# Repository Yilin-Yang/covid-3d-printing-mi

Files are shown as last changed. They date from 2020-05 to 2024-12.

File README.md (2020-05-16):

# COVID-19 PPE 3D Printing Resources (Michigan)

I'm using a GitHub repo as a file server/static site web host for files and
other materials useful for making or using 3D printed PPE.

If you're here to download files, then I'd recommend downloading "manually" by
clicking on the filename in the repo dashboard above, and then clicking
"Download" in the header bar (next to "History"). The files are stored with Git
LFS, so `git clone` from a terminal won't work correctly unless you have
[Git LFS](https://git-lfs.github.com/) installed.

## Where do I donate?

**I recommend donating to [Operation Face Shield](https://www.facebook.com/groups/1123320618008506/)**.
They're among the largest volunteer organizations for making and distributing 3D
printed PPE, they have several drop-off points (most in Ann Arbor, but also in
neighboring cities), and they have a far-reaching distribution network (mostly
in Michigan, but there's a pilot in the group who can make plane deliveries.
Outside of Southeast Michigan, Operation Face Shield has sent shipments to the
Upper Peninsula, Nebraska, and the Navajo Nation, among others.

**If you're 3D printing ear savers, then it would also be helpful if you
could send them to me.** I've set up an [ear saver request form](https://forms.gle/NtTunTbEoFRqz1C7A)
for individuals and small groups, but I actually blew through my entire ear
saver stockpile after the first night of the form being open.😅 Shoot me a  DM
on Facebook or an email (yiliny@umich.edu) if you'd like to donate, but need my
mailing address! **If you donate, please label your ear savers with the type of
plastic from which they were printed (PLA, PETG, ABS, etc.)!** This is normally
done by writing something like "PETG" on the plastic with a metallic Sharpie,
but you could also include a note that says "these are all PLA" or similar.

## What should I donate?

**As of the time of writing, you no longer need to 3D print faceshield
headbands.** A member of Operation Face Shield donated an injection mold for
faceshield headbands: using that mold, they can now manufacture ~1500 face
shields per day, which is orders of magnitude more than can be practically
manufactured by 3D printing. For comparison, it takes roughly 22 hours for
a single 3D printer to finish printing eight.

**Instead, I'd recommend printing "ear savers",** because that's what I
and OFS are short on right now. (UPDATED 5/15/20) Operation Face Shield
currently has a _long_ backlog of orders to fill, and would be thankful for any
help you can provide!

## Files

- [`ear_saver_thinn`](./ear_saver_thinn.stl) is the original STL provided by
  Operation Face Shield for its volunteers.
- [`ear_saver_thicc`](./ear_saver_thicc.stl) is a slightly modified version
  with a thicker band (1.5mm, rather than 1mm).

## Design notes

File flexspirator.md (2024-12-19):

# Flexspirator – Usage and Care

*Past versions of this page are visible in its [History](https://github.com/Yilin-Yang/covid-3d-printing-mi/commits/master/flexspirator.md).*



The "Flexspirator" is a Maker-made reusable respirator that _should_ provide
N100 protection, **though it has not been formally tested and certified by
NIOSH.** It passes a self-administered [OSHA 1910.134 App A "Irritant Smoke"
qualitative fit test.](https://www.osha.gov/laws-regs/regulations/standardnumber/1910/1910.134AppA)

The Flexspirator is designed to be worn daily by members of the general
population, to _protect_ themselves and others from COVID-19. It is intended to
be worn _instead_ of a regular cloth face mask or surgical mask, and should
offer strictly better protection.

## Motivation

Medical workers wear N95 respirators (or better) when treating COVID patients;
these protect them from contracting COVID-19 by inhaling coronavirus particles.
The N95 respirator filters the coronavirus particles out of the air they
inhale. If the respirator does not have an exhalation valve, then it will
_also_ filter coronavirus particles out of the air that the wearer _exhales_ as
well.

[**N95 respirators have been in shortage since the start of the pandemic.**](https://www.propublica.org/article/expired-respirators-reused-masks-nurses-in-the-nations-original-covid-19-epicenter-offer-sobering-accounts-of-what-could-come)
Standard medical practice is for medical workers to wear a disposable N95
respirator while treating a sick patient, and for them to _throw away_ that
respirator before treating another patient. Now, medical workers frequently
reuse the same "single-use" N95 respirator for days or weeks on end.

[As of October 27th,](https://www.cnbc.com/2020/10/27/3m-making-more-n95-masks-than-ever-as-covid-cases-rise.html)
current CDC guidelines ask that members of the general public do not purchase
N95 masks for their own day-to-day use, and instead wear cloth face masks
and/or surgical masks. This is to preserve the supply of disposable N95
respirators for frontline medical workers.

It is still probably unreasonable to expect the general public _not_ to seek
out respirators. As of November 13th, the American health care system is on the
verge of [nationwide collapse](https://www.theatlantic.com/health/archive/2020/11/third-surge-breaking-healthcare-workers/617091/)
due to uncontrolled COVID outbreaks across all 50 states. Members of the
general public should start wearing respirators: both to help protect
themselves from COVID-19 infection, and to reduce the resulting burden on the
nationwide health care system.

The Flexspirator is intended to help fill this gap. It has not been NIOSH
certified, and probably cannot be issued to actual healthcare workers without
violating OSHA regulations, but members of the general public can wear one
_voluntarily,_ and they should be protected from COVID-19 by doing so.

## Protection Offered

**The Flexspirator _should_ offer protection comparable to a reusable N100
respirator.**

This is better than the protection offered by an N95 respirator
and should be sufficient to protect the wearer from inhaling coronavirus
particles while properly worn.

It should also protect the wearer from inhaling any sort of fine particulates,
including smoke, sawdust, metal swarf (from grinding tools), and tear gas.

This is not the same _type_ of protection as offered by a respirator equipped
with (e.g.) P100 + activated carbon filters. Oily aerosols may destroy the
Flexspirator's HEPA filter, rendering it ineffective at filtration. The HEPA
filter will also not absorb chemical fumes, such as from spraypaint or Flex
Seal.

## Basic Construction

The Flexspirator is a slightly modified [Maker Mask Rapid](https://www.makermask.com/rapid-360.html)
printed from [clear PETG](https://www.amazon.com/OVERTURE-Filament-Transparent-Multipack-Dimensional/dp/B08344S1TT)
reinforced with a strong, flexible, rubberized coating of [Swift Response's Flex Seal
Liquid](https://www.youtube.com/watch?v=_NygbA9UYPw), the easy way to coat,
seal, and stop leaks fast. It's the super thick rubber that you can pour right
into cracks to stop COVID dead in its tracks.

Flex Seal starts out as a thick liquid and turns into a super strong flexible
rubber. Dipping 3D printed Maker Mask Rapids creates an airtight seal that
lasts for years.  This rubberized coating blocks ingress of contaminated air through
[cracks and holes in the plastic mask frame](https://www.preprints.org/manuscript/202006.0080/v1)
produced as artifacts of the [FDM printing](https://en.wikipedia.org/wiki/Fused_filament_fabrication)
process.

In extreme heat or cold, Flex Seal Liquid keeps its hold.

<details>
<summary>
⚠DO NOT EXPOSE A FLEXSPIRATOR TO PROLONGED TEMPERATURES OF GREATER THAN 65
DEGREES CELSIUS (149 DEGREES FAHRENHEIT); THIS MAY DEFORM THE PLASTIC.⚠
</summary>

A rough lower bound for the [glass transition temperature](https://en.wikipedia.org/wiki/Glass_transition)
of PETG plastic is 67 degrees Celsius, [according to Wikipedia.](https://en.wikipedia.org/wiki/Polyethylene_terephthalate)

Heating a Flexspirator past the PETG glass transition temperature will probably
cause the plastic to warp and deform.
</details>

Unlike thin paints, Flex Seal Liquid is **𝕤𝕦𝕡𝕖𝕣 𝕥𝕙𝕚𝕔𝕜** and creates a flexible
barrier that's _completely_ airtight. It's like a handyman, in a can!

Flex Seal Liquid is safe around plants and animals, so we used it to seal these
Flexspirators.

**Now with any COVID outbreak, big or small – Flex Seal shuts out aerosols!**

To show you the incredible sealing power of Flex Seal Liquid, we made an entire
respirator out of 3D printed PETG plastic, and covered it in Flex Seal Liquid.

After a day of creating irritant smoke clouds, and deliberately huffing them
while wearing a Flexspirator, Flex Seal's airtight barrier takes a beating; and
the HEPA filter, cut from an [ordinary replacement HEPA filter](https://www.amazon.com/gp/product/B00BWYNZV4/)
for a home air purfiier, stays filtrationally effective.

The inside will not be completely dry, because your breath will tend to
condense on the Flexspirator's inner surface.

<details>
<summary>
⚠LIMIT OR AVOID STRENUOUS PHYSICAL ACTIVITY WHILE WEARING A FLEXSPIRATOR
TO AVOID SOAKING THE FILTER WITH MOISTURE FROM YOUR BREATH.⚠
</summary>

Physical activity such as intense aerobic exercise requires heavy breathing.
Your breath carries moisture; too much may soak and moisten the HEPA filter
media, and cause it to clog; this will make breathing difficult or impossible,
and may or may not irreparably damage the filter.

If the activity cannot be avoided, be prepared to "hot-swap" the filter
cartridge if it clogs.
</details>

## Basic Usage

### Parts and Components

Flexspirator parts

The **Top Strap** and **Bottom Strap** secure the Flexspirator against your
face. They can be adjusted by pulling the ends of each strap through the
Slide Buckle, the Loop Buckle, or the Hook Buckle.

The **Hook Buckle** and the **Loop Buckle** on the Bottom Strap fasten
together behind your neck when you don the Flexspirator. This mimics the design
of a conventional reusable elastomeric respirator.

The **Mask Body** is the larger Flexspirator facepiece. It is comprised of
a stiff mask frame of PETG plastic coated on both its interior and exterior
with a silicone rubber coating of Flex Seal Liquid. Along with the Edge Lining,
the Mask Body makes up the **Facepiece** (not labeled).

The **Edge Lining** is the edge of the Flexspirator facepiece where it
contacts your face. It is comprised of [rubber kerf-mount weather stripping](https://www.amazon.com/gp/product/B06Y1SND8X)
coated with Flex Seal Liquid; the weather stripping is soft and can conform to
the wearer's face, while the silicone rubber Flex Seal coating improves its
seal against bare skin.

<details>
<summary>
Earlier Flexspirators used vinyl weather stripping, as specified by the Maker
Mask Rapid's original design.
</summary>

The [vinyl weather stripping](https://www.homedepot.com/p/M-D-Building-Products-1-2-in-x-17-ft-White-Vinyl-Gasket-Weatherstrip-78394/100193598)
was very stiff, making it necessary to cinch the Top Strap and Bottom Strap
uncomfortably tight in order to compress the Edge Lining against the wearer's
face firmly enough to seal.

The new rubber weather stripping is softer and more flexible, and unlike the
vinyl weather stripping, can reliably seal against a person's face even without
a silicone rubber coating of Flex Seal Liquid. Its use also makes the
Flexspirator much more comfortable to wear.
</details>

The **Filter Slot** is the hole into which the Filter Tray is placed. The space
between the Filter Tray and the Filter Slot (not labeled) is the
**Cartridge/Slot Interface**; this must be filled with a **Cartridge/Slot
Interface Sealant**, such as petroleum jelly applied to the lip of the
Filter Tray, to prevent contaminated air from flowing around and bypassing the
filter media.

The **Filter Tray** houses the **Filter Media**, which actually filters air.
The Filter Media is compressed flush against the walls of the Filter Tray by
a plastic **Retaining Ring**. Without this Retaining Ring, the Filter Media may
lift and curl away from the walls of the Filter Tray, creating air gaps, which
may allow contaminated air to bypass the Filter Media.

The **Filter Cover** is functionally a "nut" that screws onto the lip of the
Filter Tray where it protrudes beyond the front of the Flexspirator. It does
not help to filter air, but simply holds the Filter Tray snugly against the
walls of the Filter Slot. We call a Filter Cover screwed onto a Filter Tray
a **Filter Cartridge.**

The **Locking Dimple** is a small divot in the front of the Mask Body. The
Filter Cover has a corresponding **Locking Bump** that seats into the Locking
Dimple when the Filter Cover is screwed onto the Filter Tray, helping to lock
the Filter Cover into place.

### Assembly and Disassembly, Replacing Filter Cartridges

This summarizes the process of loading a new Filter Tray into the Flexspirator.
Removing an already installed Filter Tray is essentially the reverse of
this process.

**1. With the Mask Body cupped in one hand, place a Sealant-coated Filter
Tray into the Filter Slot.**



**2. Press the Filter Tray firmly into the Filter Slot.**



If you have just applied petroleum jelly Sealant to the lip of the Filter Tray,
then you should see the excess jelly squeeze out from _all_ sides of the
Cartridge/Slot Interface. If it does not, or if it squeezes out on some sides
but not on others, then remove the Filter Tray and apply more petroleum jelly
where needed.

**3. The lip of the Filter Tray should visibly protrude from the front of the
Mask Body.**



During disassembly, you can pop the Filter Tray out of the Filter Slot without
getting petroleum jelly on your hands by striking the exposed lip of the Filter
Tray with the Filter Cover.

**4. Place a Filter Cover over the lip of the Filter Tray as pictured so that
the "nubs" of the Filter Cover point toward 11 o'clock and 5 o'clock
positions.**



**5. Grip the nubs of the Filter Tray.**



**6. Twist the Filter Tray clockwise, as viewed from the front of the Mask
Body, until the Locking Bump slides into the Locking Dimple.**



You may hear or feel the Locking Bump click into place. If the Locking Bump
does not fit into the Locking Dimple because the Locking Dimple is packed with
Flex Seal, then you may scrape out the excess Flex Seal with a small pick or
knife.

**Do NOT** twist the Filter Cover so that the Locking Bump moves _past_ the
Locking Dimple. This may damage the lip of the Filter Tray.

It is possible for the Locking Bump to break off of the Filter Cover. In this
case, the Filter Cover can still be used, but may not hold the Filter Tray as
solidly. Note that Filter Covers are fully interchangeable, so a Filter Cover
from a replacement Filter Cartridge can replace a broken Filter Cover without
issue.

### Maintenance

Protect the Flexspirator from damage so that it can still maintain an
airtight seal against the wearer's face when worn.

The seal may be compromised by:

1. _Physical damage to_ OR _manufacturing defects in_ the plastic mask frame,
resulting in micro- or macro-scale cracks and holes.
2. _Peeling_ or _perforation_ of the Flex Seal coating.
3. _Pinhole leaks_ in the _filter cartridge/slot sealant_, which may allow air to
bypass the HEPA filter media by passing between the filter tray and the filter
slot.

Even the plastic mask frame should be largely airtight by
itself. This creates protective redundancy: both (1) and (2) must occur at the
same spot on the mask's surface for the walls of the mask to spring a leak.
To check for such leaks, conduct an **Integrity Test** as described below.

Of course, tears, punctures, or other forms of damage to the Filter Media can
make it ineffective at filtration. Actual holes would allow contaminants to
bypass the filter, for instance, or destroy the mesh of fine fibers in the
Filter Media that would actually trap contaminants. Take care to avoid damage
to the Filter Media when cleaning, disinfecting, or wearing the Flexspirator.

#### Avoiding Damage to the Filter Media

_When researching how to work with HEPA filter media, I used [this link](https://smartairfilters.com/en/blog/hepa-filters-make-diy-face-masks-covid-coronavirus/)
as an informational reference._

The Filter Media is cut from an ordinary replacement [HEPA
filter](https://www.amazon.com/gp/product/B00BWYNZV4/) for a household air
purifier. It consists of a stiff, "papery" structural layer of PET fibers that
supports a thin, extremely delicate "tissue" of polypropylene (PP) fibers. The PP
fibers are the "actual" filter media that would trap contaminants like
coronavirus particles. The PET backing provides some filtration, but this is
probably incidental, and for safety we should assume that the filter media is
ineffective without an intact PP "tissue".



HEPA filters intended for actual use are typically pleated, i.e. folded like an
accordion, to maximize the surface area of filter media in which contaminants
can be trapped. In filters like the [Honeywell replacement filter](https://www.amazon.com/gp/product/B00BWYNZV4/)
that I cut apart for Filter Media, each individual fold of the "accordion" is
supported by strips of thick glue from the fold underneath.

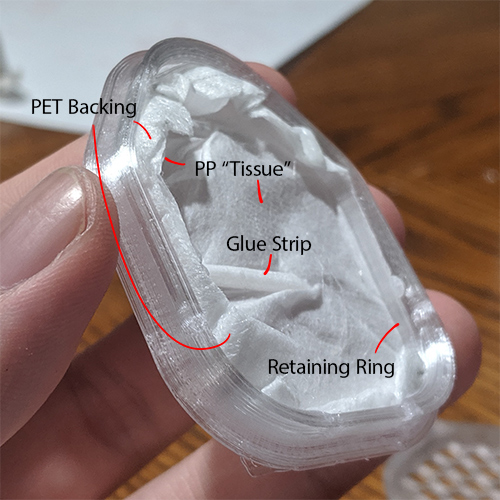
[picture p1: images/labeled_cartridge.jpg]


If you need to remove the Filter Media from a Filter Tray, then _after_
removing the Retaining Ring, you can use a thin object (like a screwdriver) to
push the Filter Media out of the tray, pressing the object's tip into a glue
strip, avoiding damage to the PP "tissue". You should also be careful to
unstick the glue strips from the inner surface of the Filter Tray "lip", if
applicable, so that the PP "tissue" does not rip as the Filter Media is removed
from the Filter Tray.

To protect the Filter Media from damage and preserve its effectiveness
at filtration:

- **Do NOT** prod or scratch at the soft, felt-like "tissue" in the Filter Tray
- **Do NOT** soak or splash the Filter Media with water or other liquids
- **Do NOT** expose the Filter Media to soaps or disinfectants
- **Do NOT** expose the Filter Media to oily, sticky, tarry, or resinous aerosols, such as
  from blowing cigarette smoke through the Filter Media

#### Avoiding Structural Damage to the Plastic Mask Body

The Flexspirator is reasonably durable and will comfortably survive _ordinary_
rough handling, but extreme mishandling can snap, break, or deform the
underlying plastic mask frame. **Forms of mishandling that may break the plastic
mask body include:**

- Stepping on a Flexspirator _with_ your body weight
- Striking a Flexspirator sharply with a claw hammer
- Stowing a Flexspirator in a cramped book bag with heavy textbooks
- Exposing a Flexspirator to prolonged temperatures over 65 degrees Celsius
(149 degrees Fahrenheit)

The following will **probably NOT cause structural damage** to a
Flexspirator:

- Hurling a Flexpirator into a drywall from five meters distance
- Crashing face-first into a sliding glass door while wearing a Flexspirator

#### Avoiding Damage to the Flex Seal Coating

Flex Seal Liquid costs around $90 per gallon. Based on preliminary estimates,
it takes approximately $5 of Flex Seal Liquid to coat a Flexspirator. The
coating is made as thin as possible to maximize the number of Flexspirators
that can be constructed from a single bucket of Flex Seal Liquid; and for
cosmetic reasons, like avoiding bubbles and blobs.

The coating of cured Flex Seal Liquid will most likely peel and rip:

- Near the edges of the coating, where the cured Flex Seal gives way to
uncovered plastic.
- On the surface of the flexible vinyl weather stripping; too much
deformation of the weather stripping can overstress the Flex Seal and make it
tear.

The Flex Seal coating will **probably be damaged** by:

- Scraping with a metal fork or knife
- Scraping the Flexspirator against an abrasive surface with pressure, as by
forcibly scrubbing the Flexspirator against a bare brick wall

The Flex Seal coating will **probably _NOT_ be damaged** by:

- Rubbing or picking with your hands, unless you are picking at existing tears
or the edges of the coating
- Scrubbing with the scouring pad of a kitchen sponge, even one that isn't safe
for non-stick pans
- Rubbing against the spiral metal ring binding of a loose-leaf notebook while
in a book bag

#### Maintaining the Filter Cartridge/Slot Sealant

This section explains the purpose of the petroleum jelly Sealant in the
Flexspirator design, how to maintain it, and how to reapply it when necessary.

Imprecision in the process of 3D printing would prevent a perfect airtight seal
at the Cartridge/Slot Interface, i.e. between the plastic of the Filter Slot
and the Filter Tray. Without that seal, contaminated air may flow _around_ the
Filter Tray, bypassing the Filter Media entirely. We apply a Cartridge/Slot
Interface Sealant to fill these air gaps. In principle, many materials could be
used as Sealant, but we recommend common household petroleum jelly.

Gaps in the petroleum jelly Sealant may permit contaminated air to bypass the
Filter Media. This risk can be cheaply mitigated by applying _generous_ amounts
of petroleum jelly as Sealant, increasing the volume of jelly that would need
to be displaced to produce a leak.



You can apply a coating of Cartridge/Slot Interface Sealant simply by smearing
_generous_ quantities of petroleum jelly on the lip of a Filter Tray with
a Q-tip. As you press the Filter Tray into the Filter Slot, petroleum jelly
should squeeze out from the Cartridge/Slot Interface.



**You should reapply the petroleum jelly Sealant after:**

- Switching Filter Cartridges, if the lip of the new Filter Tray has not
  been coated with petroleum jelly.
- Washing the Flexspirator, e.g. in a kitchen sink, with a sponge and
  dish soap. Actions like this will wash away petroleum jelly.
- Removing and reinserting the same Filter Tray more than a half-dozen times
  without any reapplication of petroleum jelly.
- Seeing that the petroleum jelly is visibly dirty.
- Hearing a hissing sound from the Filter Cartridge when inhaling that does not
  sound like regular air movement, OR, Feeling a thin jet of "cold air" on your
  face inside the Mask Body that seems to come from the Cartridge/Slot Interface.

To "refresh" the Interface Sealant in between reapplications of petroleum
jelly, you can insert the Filter Tray into the Filter Slot and then "smear" the
excess petroleum jelly around the back edges of the Filter Tray. This is
usually sufficient to seal pinhole leaks when both the Filter Slot and Filter
Tray have existing coatings of petroleum jelly.

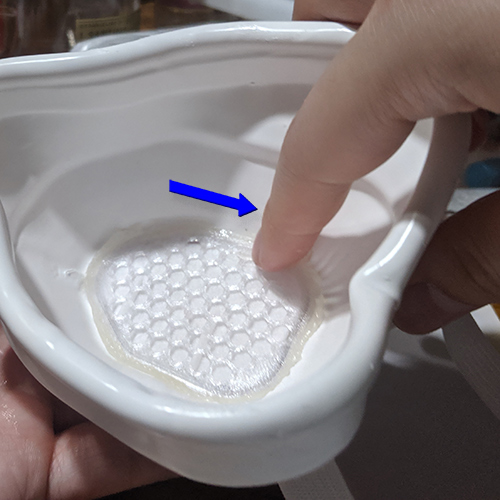
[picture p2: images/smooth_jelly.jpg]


Excess petroleum jelly that spills onto other parts of the Mask Body interior
can be wiped away without issue.

### Seal and Integrity Check

This section explains how to don a Flexspirator and then perform a seal check.
It also explains how to perform an integrity check, which is extremely similar
to a seal check.

#### Performing a Seal Check or Integrity Check

You should perform a **seal check** after donning a Flexspirator, to make sure
that the Edge Lining has sealed properly against your face. To perform a seal
check, don a Flexspirator already loaded with a Filter Cartridge, tightly cover
the front of the Flexspirator ("smothering" the Filter Cover) with your hand,
and try to inhale or exhale. Your hand will probably not completely block air
movement through the Filter Cartridge, but it should _reduce_ it; you should
notice the Flexspirator "suck in" against your face when inhaling, or "bulging
out" against your hand when exhaling. If the Flexspirator does not "suck in" or
"bulge out", then the seal check has failed.

<details>
<summary>
⚠A SUCCESSFUL SEAL CHECK DETECTS OBVIOUS PROBLEMS, BUT DOES NOT NECESSARILY
MEAN THAT THE CARTRIDGE/SLOT INTERFACE HAS BEEN PROPERLY SEALED.⚠
</summary>

Small leaks, like pinhole leaks in the Cartridge/Slot Interface Sealant, may
not be noticeable during a seal check.
</details>

You can perform an **integrity check** by following the same procedure as
a seal check, except that you should don the Flexspirator with the Filter
Cartridge _removed,_ i.e. with the Filter Slot completely empty. This should
allow you to fully plug the front of the Flexspirator with your hand, making it
entirely airtight. If you try to inhale or exhale, you should feel _no_ air
movement _whatsoever_ through the Flexspirator. If you feel air movement, then
the integrity check has failed.

The following are illustrations of the basic process of conducting a seal check
or an integrity check.

**1. Pull the Top Strap over the crown of your head.**



**2. Adjust the Top Strap, securing the upper half of the Flexspirator against
your face and nose.**



Use both hands to grab separate ends of the Top Strap. Pull outward, to lift
the Slide Buckle away from the scalp, so that the Top Strap does not snag your
hair during adjustment.

**3. Fasten the Hook Buckle and Loop Buckle behind your neck.**



**4. Adjust the Lower Strap, securing the lower half of the Flexspirator
against your cheeks and chin.**



**5. Press your hand into the front of the Flexspirator and inhale or exhale,
to see if the Mask Body "sucks in" or "bulges out", respectively.**



#### Implications of Failing a Seal Check

If a seal check fails, then the Flexspirator will not protect you as you are
currently wearing it. **Do not wear the Flexspirator in a hazardous environment
if you are not able to pass a seal check.**

Performing a seal check helps you to detect _obvious_ problems with the seal
of a Flexspirator. These might be large cracks and holes in the Facepiece that
contaminated air can penetrate; or the Flexspirator may not
[fit](https://www.osha.gov/video/respiratory_protection/fittesting_transcript.html)
properly; or the Flexspirator may not be seated properly on your face.

Large cracks and holes in the Flexspirator will need to be repaired. This is
probably most easily done by painting the broken area with a new coating of
Flex Seal Liquid and allowing it to cure in a well-ventilated space for 24-48 hours.
[32 oz. cans of Flex Seal Liquid](https://www.homedepot.com/p/FLEX-SEAL-FAMILY-OF-PRODUCTS-Flex-Seal-Liquid-White-32-oz-Liquid-Rubber-Sealant-Coating-LFSWHTR32/301711550)
are typically available at Home Depot for $30; this is enough to repair
dozens or hundreds of broken Flexspirators, so if Flexspirators are being
worn by your colleagues or neighbors, then you can pool your money to buy
a single can for your collective use.

You may be able to fix the Flexspirator's seal by adjusting the Mask Body's
position on your face, or loosening/tightening the Top Strap and Bottom Strap
as needed.

If the Flexspirator does not fit properly – meaning that, no matter how you
adjust it, there are still air gaps between the Edge Lining and your face
– then you may try to fill those gaps with [**Duct Seal**](https://www.homedepot.com/p/Gardner-Bender-1-lb-Plug-Duct-Seal-Compound-DS-110/100212441),
a cheap dough-like material akin to [Blu Tack](https://en.wikipedia.org/wiki/Blu_Tack)
used to fill "gaps and holes" in ductwork.

#### Implications of Failing an Integrity Check

**If an integrity check fails, then contaminated air will be able to penetrate
the Flexspirator without passing through the Filter Media.** The Flexspirator
may still provide better protection than a cloth face mask or surgical mask,
but will no longer reliably provide N100 or even N95 protection unless it is
repaired.

An integrity check is similar to a seal check, but it only tests for leaks in
the Facepiece. Because no Filter Cartridge is loaded when conducting an
integrity check, this check is useful mainly for testing damaged Flexspirators
to see if they can still be safely worn, or to see if attempted repairs were
successful.

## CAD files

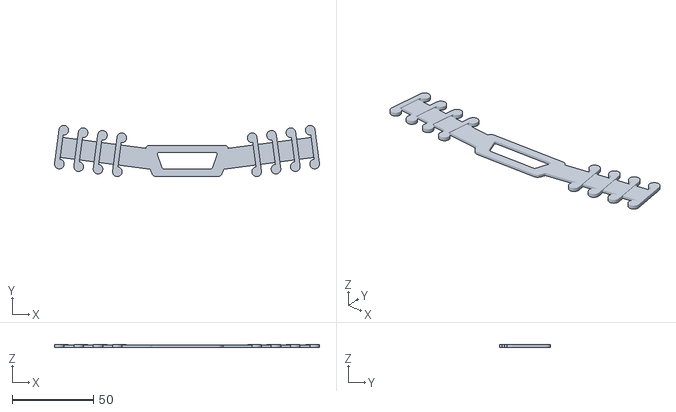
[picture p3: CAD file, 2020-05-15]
3d_print_files/ear_saver_thicc.stl
163.0 x 31.5 x 2.00

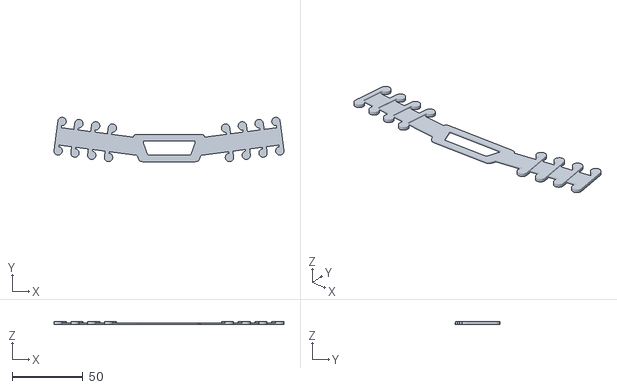
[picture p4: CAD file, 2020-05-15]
3d_print_files/ear_saver_thinn.stl
163.0 x 31.5 x 2.00

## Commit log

2020-11-21 Create subdirs for static files; add mask images
    [ear_saver_thicc.stl, ear_saver_thinn.stl]
2020-11-21 Remove numbering from assembly images
2020-11-22 Add seal/integrity check instructions
    Add illustrated instructions on performing seal and integrity checks.
    Also:
    - Minor rewording.
    - Add missing part documentation for the Filter Cover.
    - For consistency and clarity, refer to the protruding part of the
    Filter Tray as a "lip" and not "the edges".
2020-11-25 Add labeled image of Filter Tray
2020-11-25 Write care instructions for HEPA filter media
    Also, reformat <img> HTML tags to put the `width=` attribute in front of
    the `src=`, since that makes them easier to see and edit.
2020-11-26 Add assembly instructions; document Locking Bump
    Also,
    - Update images/flexspirator_parts.png to label the Locking Bump.
    - Move "Protection Offered" section to top-level from "Basic Usage"
    because that information is important and shouldn't be buried.
    - Explain when to reapply petroleum jelly Interface Sealant.
    - Explain "smearing' petroleum jelly sealant around mask interior.
    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
2021-02-27 Elaborate on repairs; more verbose collapsibles
    - Talk more about the process of repairing Flexspirators. Drastic
    repairs (for Flexspirators that have completely broken) are probably
    unnecessary for nearly all users; painting over perforations with Flex
    Seal Liquid is probably the most that any person would need.
    - Make collapsible text box summaries more verbose, so that it isn't
    necessary to click-to-expand to understand the point of the warning. If
    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
2024-12-19 Fix typos ("aroud", "keft")
    Not sure where I got "keft-mount" from when I meant to write "kerf-mount." Maybe it was a weird autocorrect thing?
